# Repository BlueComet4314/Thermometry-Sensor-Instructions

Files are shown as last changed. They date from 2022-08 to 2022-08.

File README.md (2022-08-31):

# Table of Contents

<u>**Intro**</u>
- [Overview of Thermometry Sensors](#overview)
- [Accessories used](#accessories-used)
- [Sensor Board Versions](#sensor-versions)
- [Test data](#tests)
    
    - [Room Temperature Test](#u-room-temp-test-u)
    - [Liquid Nitrogen Test](#u-liquid-nitrogen-test-u)
    - [Vacuum Test](#u-cold-test---inside-vacuum-for-nexo-distillation-column-u)
     
      - [Thermosiphon Set up](#thermosiphon-set-up)

<u>**Instructions**</u>

- [Thermometry Sensor](#thermometry-sensor-1)
- [Thermocouples](#thermocouples)
- [PT100 (RTD) Boards](#pt100-rtd-boards)

  - [RTD Sensor](#sensor)
  - [Parts](#parts)
  - [Oshpark Schematic](#oshpark-schematic)
- [Wiring](#wiring)

  - [QWIIC cables to 3 Wire cable](#pt100-board-to-db15-wires-3-wire-configuration)
  - [DB15 Connector Layout for soldering](#db15-layout)

    - [Visual of wires connected to DB15](#to-db-15-images)
- [Casing](#casing)

- [Test Board](#test-board)

<u>**Final Documentation**</u>

- [Set-up Instructions](#set-up-instructions)
- [Final Images](#final-images)
- [Flange](#flange)
- [Trouble Shooting](#trouble-shooting)

# Overview

## [Original Github - bungernut/nEXO_Thermometry](https://github.com/bungernut/nEXO_Thermometry)

These sensor boards were built to read and display thermometry data. They were orignialy used for an experiment made by LUX-ZEPPLIN (LZ) to measure data within their cryogenic systems. Later, a group from the nEXO group based their design (with permission) off of the group from LZ. 

This document details the process of parts, construction, set-up, and uses of these boards for the nEXO experiment at the SLAC National Accelerator Laboratory. The boards at nEXO are used for cryogenic purposes inside of a cryogenic distillation column. 

**Please don't hesitate to contact me with any questions you may have!!**

The Thermometry Boards are able to detect temperature, pressure, and humidity using five Adafruit MAX31865, two MAX31856 boards (Thermocouple Amplifires), and one BME 280.

The pads are soldered to a small .5" circuit board and connected to the main Thermo board through a series of cables (which will be detailed out below). The small PT100 boards contain a 4-40 sized hole for a small screw, which will allow the boards to be attached to specific places inside of the cryogenic system (more into this later). 
The thermocouples are attached to two Adafruit MAX31856 - Thermocouple Amplifier boards. 

[Back to Top](#table-of-contents)

# Accessories used

## Thermometry Sensor:

### - Normal parts
| LOC | Part | Digikey PN |
| -- | -- | -- |
| J1 |  DB15 | LD15S33E4GV00LF-ND |
| J2 | Barrel 2x5.5mm | CP-002A-ND |
|Teensy Conn| 24POS RCPT| SAM1093-24-ND|
|Teensy Conn| 6POS 2mm RCPT| 23-0791077002-ND |
|Teensy header| 30POS 2.54mm | S1012EC-30-ND |
|Teensy header| 6POS 2mm | WM20513-ND |
| Ethernet Conn | 100 Base T | 1278-1052-ND |
| LCD Conn | 2x CONN HEADER 14POS | AE11367-ND|
| R1-12 | 22 Ohm 0805 | A126437CT-ND |
| R13 | 0 Ohm 0805 | A106066CT-ND |
| CP1 | 47 uF 1206 | 490-16309-1-ND |
| F1 | 1A Fuse | F6777CT-ND |
| C1 | 0.1 uF Ethernet Cap | BC1084CT-ND |
| MCU1 | 2x 24POS Recpt | SAM1093-24-ND |

### - Sensor Boards
| Board Type | Purpose | Digikey Pin |
| -- | -- | -- |
| Adafruit MAX31865 | RTD | 1528-1804-ND |
| Adafruit MAX31856 | Thermocouple Amplifier | 1528-1772-ND |
| Adafruit BME 280 | Temperature, Humidity, Pressure | 1528-1359-ND |

### - Microcontroller

Teensy 4.1 -
  - 1568-DEV-16771-ND

## - PT100 Boards

### - Equipment

- Need a USBC cable for power and uploading arduino software onto microcontroller
- An Ethernet Cable
- Computer or laptop compatible with Arduino software
- Soldering Iron
- tweezers
- needle nose pliers

[Back to Top](#table-of-contents)

# Sensor Versions

## <u> V1 with old test board: </u>

 


## <u> V2 with new test board: </u>

 

## <u> V3 with test thermocouples and Copper block inputs </u>



(picture of copper blocks)

## <u> V4 - Finished (Final) Board: </u>

- Completed PT100 pads/circuit boards and two thermocouples

 

[Back to Top](#table-of-contents)
# Tests

## <u> Room Temp Test </u>

- With PT100 inputs and short Thermocouples

### readings:

| Sensor | 1st Reading | 2nd Reading | 3rd Reading | Actual temperature | 
| -- | -- | -- | -- | -- |
| RTD 1 | 296.58 K | 296.48 K | 296.31 K |  | 
| RTD 2 | 295.57 K | 295.54 K | 295.64 K |  |
| RTD 3 | 296.08 K | 296.11 K | 296.42 K |  |
| RTD 4 | 296.01 K | 295.98 K | 295.87 K |  |
| RTD 5 | 295.98 K | 295.94 K | 296.04 K |  |
| TC 1 | 295.45 K | 295.53 K | 295.86 K |  |
| TC 2 | 295.09 K | 295.11 K | 295.17 K |  |

## <u> Liquid Nitrogen Test </u>

- With Original Copper PT100 blocks and long Thermocouples
- Finished Thermo Sensor, tested temperature readout with Liquid Nitrogen - ~ 77 Kelvin. 
  - Small margin of error on TCs +/- 3 Kelvin.

Liquid Nitrogen ranfes from 63 K - 77.2 Kelvin

###  Readings:

| Sensor | 1st Reading | 2nd Reading | 3rd Reading | Actual temperature | 
| -- | -- | -- | -- | -- |
| RTD 1 | 76.00 K | 75.97 K | 76.06 K | 77.2 K |
| RTD 2 | 76.18 K | 76.15 K | 76.27 K | 77.2 K |
| RTD 3 | 76.09 K | 76.09 K | 76.18 K | 77.2 K |
| RTD 4 | 76.03 K | 76.03 K | 76.09 K | 77.2 K |
| RTD 5 | 75.75 K | 75.69 K | 75.72 K | 77.2 K |
| TC 1 | 81.86 K | 81.72 K | 82.15 K | 77.2 K |
| TC 2 | 80.08 K | 80.31 K | 80.28 K | 77.2 K |

## <u> Cold Test - Inside vacuum for nEXO Distillation Column </u>

### Thermosiphon set up:



The thermosiphon acts as an evaporator for the Liquid Xenon Cell in which it is located. The thermosiphon will be pumping Liquid Nitrogen through it's main two tubes connected at the top:



Once the entire distillaiton column is completed, Gaseous Xenon will be pumped into the main chamber (where the Thermosiphon is located) inside of a smaller enclosed space. This is attached directly below the thermosiphon.

PT100 sensors are screwed into specific places on the thermosiphon. To test, we used PT100 sensor blocks used by a different experiment - LZ. We compared the new PT100s (RTDs) to the previous ones - with the knowledge that LZ's worked - in order to discern any unusual readings from the new PT100s.

### ***Note***

When installing RTDs (or anything) inside of the distillation column, it is a good idea to clean with ethanol on kimwipes.

There are two PT100's from LZ, and four PT100s from nEXO. From now on, I will label the new PT100s as RTD, and the old RTDs as LZ. They are labeled on the Thermosiphon as shown:

### Front Side view:



### Back Side view:



LZ1 and RTD 4 are in parallel with each other on the Aluminium block - They should be reading relatively the same temperatures.
LZ2 and RTD 1 are also in parallel with each other on the Copper block - They should be reading the same temperatures as well.

#### **Note:**



- The *top* of the Thermosiphon - (Copper block) is where the cool Liquid Nitrogen will enter, this is the coldest area
    -  RTDs 1 and 2, and LZ 2 are located here
- The *very bottom* of the block (aluminium block) is where the heater is located - the warmest area.
    - RTDs 3 and 4, and LZ 1 are located here

### Set Thermosiphon temperature at 170 K	(Aluminium block).

| PT100 |	Measurement (K) |
| -- | -- |
| RTD1	| 158.16 |
| RTD2	| 147.29 |
| RTD3	| 169.99 |
| RTD4	| 170.31 |
| -- | -- |
| LZ1 |	170.83 |
| LZ2 |	157.61 |

- This is very promising information - RTDs 3 and 4, and LZ 1 are located directly on the heater, reading near exactly 170 K. In addition, LZ1 and RTD4 sensor readings are very close to each other - roughly .5 K apart from one another

[Back to Top](#table-of-contents)

# Instructions: 

# Thermometry Sensor

### OshPark link:

[Thermometry_Board_V2](https://oshpark.com/shared_projects/bG9Ms06A)

### Finished schematic:

 

### Initial Board:



 

Parts:
| LOC | Part | Digikey PN | Color on Schematic |
| -- | -- | -- | -- |
| J1 |  DB15 | LD15S33E4GV00LF-ND | yellow |
| J2 | Barrel 2x5.5mm | CP-002A-ND | Dark Blue |
|Teensy Conn| 24POS RCPT| SAM1093-24-ND| Orange |
|Teensy Conn| 6POS 2mm RCPT| 23-0791077002-ND | Purple |
|Teensy header| 30POS 2.54mm | S1012EC-30-ND | Orange |
|Teensy header| 6POS 2mm | WM20513-ND | Purple |
| Ethernet Conn | 100 Base T | 1278-1052-ND | Red |
| LCD Conn | 2x CONN HEADER 14POS | AE11367-ND| Green |
| R1-12 | 22 Ohm 0805 | A126437CT-ND | -- |
| R13 | 0 Ohm 0805 | A106066CT-ND | -- |
| CP1 | 47 uF 1206 | 490-16309-1-ND | Teal |
| F1 | 1A Fuse | F6777CT-ND | Pink |
| C1 | 0.1 uF Ethernet Cap | BC1084CT-ND | Light Blue circle |
| MCU1 | 2x 24POS Recpt | SAM1093-24-ND | -- |

[Back to Top](#table-of-contents)
## Highlighted Schematic:



 

## Soldering:
The order in that I added pieces (this is not the best order to go in).
- **22 Ohm Resistors** onto pads R1-R12, skipping R-13
- **0 Ohm Resistor** onto R-13 pad
- **DB15 Connector** on the J1 pad
- **LCD Connectors** on the ILI9341TFT1 and ILI9341TFT2 pads
  - Make sure the keying slot is facing the right direction. On the main board, the slot should be facing *toward* the MAX31865 pads and *away* from the Teensy pad.
  - On the **small** board, make sure the slot is facing *away* from the ILI9341TFT3 Through Holes.
- The **1A Fuse** on the F1 pad 
- A **47 uF capacitor** on CP1 pad, below the Fuse.
- **0.1 uF Ethernet Capacitor** on pad C1.
  - The name of the pad isn’t visible on the schematic; the capacitor is next to the Ethernet Plugin
- An **Ethernet plugin** on the Teensy-Ethernet1 pad.
  - The opening of the connector should also be facing *away* from the board.
- A **Black Barrel Power Jack connector** on the J2 pad.
  - Make sure that this connector is also facing the correct direction; the main connector should be facing *away* from the middle of the board
- The **Receptacle Connectors** are placed on the long row of ThroughHole pins on the Teensy pad:

 

- Similarly, long **connector headers** (length 24) and smaller (3x2) connector headers will be soldered to the Teensy 4.1 board:
  - The 3x2 connector has it's *shortest* side soldered to the Teensy
  - The long 24 pin connector has it's *longest* side solder to the Teensy

 

- The pins (connected to the Teensy) will be put into the Recepticle connectors already soldered to the main board:

  

[Back to Top](#table-of-contents)

### Sensor Boards:

#### Parts Used

| Board Type | Purpose | Digikey Pin | Amount |
| -- | -- | -- | -- |
| Adafruit MAX31865 | Resistance Temperature Detector | 1528-1804-ND | Five |
| Adafruit MAX31856 | Thermocouple Amplifier | 1528-1772-ND | Two |
| Adafruit BME 280 | Temperature, Humidity, Pressure Detector | 1528-1359-ND | One |

- Five Adafruit MAX 31865 boards (Resistance Temperature Detectors (RTDs)) are soldered to their respective places along one end of the main board.
  - These for pin holes are normally where two wire clamps would go. However, instead, we are going to put 3 Connector headers here.  The MAX 31865 boards do not have Connectors that are wide enough for the 4 pins, so break apart the receptacle headers into singular pieces.



  

The individual pins will go in three specific places; one pin in the F- hole, one in the RTD+, and the last in th F+ hole. The front of the Adafruit board has just the F- and F+ label - the RTD+ hole is directly to the left of the F+ slot (see image). The full labels can also be seen on the very back. 







- Two Adafruit MAX31856 boards (Thermocouple Amplifiers) are soldered to other side of board:

 

- One BME 280 Board (Temperature, Humidity, Pressure):




## MAX31856 - RTD Board
- The RTD boards (in our version) were modified for a 3 wire configuration.
- Initially, the connection line on the copper plates - between the 4 and 3 wire pads (ass seen in below images) - needs to be severed.
  - Taking an exact-o knife, the copper line is cut/scraped away.

## Before

 

 

## After


 
 

- The two 3 wire pads need to then be soldered together



Nothing needs to be changed for the BME or Thermocouple amplifiers

[Back to Top](#table-of-contents)

# Thermocouples

The thermocouples used in this sensor are type 'T', with Copper and Constantan (Cu-Con) metals. This type of thermocouple can measure tempuratures from -250 degrees Celsius (23.15 K) to 350 degrees Celsius (623.15 K), which is very helpful to measure accurate temperatures in cryogenic conditions.

Thermocouples themselves always consist of two different types of metals that are joined together at one end - whether with solder or welding is up to the person. When the soldered end of the thermocouple is heated or cooled a voltage is created that can be associated with a specific temperature.

The thermocouples in our system will be used in conjunction with the Adafruit MAX31856 (Thermocouple Amplifier) boards. We'll need two - preferably long (roughly two and a half feet long) in order to test temperature readings. You can also make two short thermocouples in order to quickly test room temperature without the hastle of the long wires.

First, strip both ends of the thermocouple wires - the outer plastic, then the individuals (as shown in the images below).

Leave one side of the wire alone, that will be inserted into the connectors on the thermocouple amplifiers.
On the other end, twist the two metals and solder the wires together.

 
 

  

The two ends that were not soldered together will be inserted into the terminal block (the black fastener), the Copper wire will be placed in the positive port (right hole) and the Constantan wire will be placed into the negative port (left hole).

Screw the top until the wires rest tightly inside the terminal block.

 



Full Sensor with short thermocouples and Test board:



Full sensor with long thermocouples, connected to copper sensor blocks:



[Back to Top](#table-of-contents)

# PT100 (RTD) Boards

These boards were designed to measure and read out temperatures taken from a PT100 (RTD) sensor, which is transmitted to the Adafruit MAX 31865 boards using a QWIIC JST Conncector. The board itself is designed to lever and flatten the white RTD pad against the surface of an object (as seen in images below). 

The board was designed with a 4-40 screw hole in order to lever the PT100 pads onto the surface (in nEXO's case - the Thermosiphon as explained [above](#thermosiphon-set-up)):





----




Full Set Up







### Boards:



### Sensor:



---
## Parts:
---

| Part | Store | Pin |
| -- | -- | -- |
| PT100 - RTD | Digikey | 1759-1021-ND |
| Qwiic JST Connector | Mouser Electronics | 474-PRT-16766 |
| 4 Position Cable | Digikey | 1568-PRT-17257-ND |

[Back to Top](#table-of-contents)

### <u> OshPark Schematic:</u>

[PT100 Level Board - V2](https://oshpark.com/shared_projects/1DKsv6yt)

### <u> Instructions:</u>

Only two parts need to be soldered to the PT100 board; the QWIIC connector and the Resistance Temperature Detector (RTD). 

There are two small holes where the wires of the RTD will be placed through.
When placing the wires in, make sure that the white side of the RTD is facing toward the 4-40 hole and the blue side is facing away from it. That way when the pad is bent, the white side will be facing upward.



Next is the surface mounted QWIIC connector.
The pins should be soldered in their respective places, including the pins on the back of the connector:



### ***Note 1***

Mke sure that the RTD is pulled through the two holes on the PT100 board as far as possible without breaking it.
When bent, the two wires may still jut out a bit on the copper side of the board, we don't want any metal touching the wires and causing a short (see image):

### ***Note 2***

Make sure that the ends of the RTD wires are clipped after you solder. Leaving the wires hanging can also cause a short if they touch any metal.

### <u> Comparisons: </u>

with penny:




 

[Back to Top](#table-of-contents)

### <u>completed</u>

 

back 

side 

Make sure that the ends of the RTD wires after soldered are snipped short.

[Back to Top](#table-of-contents)

full comparisons:

     



[Back to Top](#table-of-contents)

# Wiring

## PT100 Board to DB15 wires (3 wire configuration)

### Materials:

- Heat-shrink
- Three Wire cable
- 4 position cable (digikey)

The PT100 wires are connected to the Adafruit board with a 3 wire configuration. 
The four position (4P) cable bought from digikey site contains four wires and has two male QWIIC connectors on either side - the length of the wire will need to be cut in half.

---

The reason for a 3 wire configuration over simply just having two has to do with the added resistance in the wires themselves. 



In a three or four wire configuration, the extra third and fourth wires detect the added resistance in the main (1st and 2nd) wires so that we are able to later account for it. 
However, a four wire configuration is very complicated to put together. 
Therefore, a 3 wire config is used. 

With a 3 wire, we assume that the added resistance in the first wire is the same as what is detected in the third wire.

More information on these configurations can be found [<u><big>***here***</u></big>](https://www.omega.com/en-us/resources/rtd-2-3-4-wire-connections)

---

As seen in the below photos, the blue wire from the 4P cable was folded back, the three left were stripped and tinned.

Three wire braided cable can be used to make the 4P cable longer. For the nEXO group, 25 inch wire was needed, but the 4P wires were only 6 inches. Measure and cut needed length as necessary.

### _**Note**_:

The colors of the three wire cable doesn't matter, but it would be better to find colors that match with the QWIIC (4P) cable (or any other cable used) to keep colors consistent and easy to follow for later on.

Recommended colors would be - black, red, and white cable. 
The 4P cable is colored black, red, blue, and yellow, but the blue wire was not used; red to red, black to black, and yellow to white.

 The 3 wire cable was also stripped and tinned, but before soldering them together, make sure heat shrink plastic tubes are put on the individual wires. 
 The heat shrink should be think enough to fit over the wire and still have some room to maneuver. 
 It should then be soldered to the 4P cable as seen in the images below.

 The other end of the three wire should not be soldered to anything yet.





[Back to Top](#table-of-contents)

Move the heat shrink so that it covers the exposed wire and both cables that were soldered together. 
Heat the shrink plastics so that they are snug on the wires and do not individually move.
The wires can all three be moved in front of the heat gun at the same time, as long the heat shrink plastics are not touching each other.

Then, cut another piece of heat shrink and place it over the three wire cable (white, red, black) all the way until just before the the soldered joints - not entirely over the connected wires. 
This is to help keep the wires themselves protected and to keep them held together.
It is circled in the next photo:



This also needs to be shrunk with the heat gun. Another wider tube of heat shrink needs to be cut. this time placed over the entirety of the wires - **_including_** the blue wire that was not used from the 4P QWIIC cable. The blue wire is included so that there are no exposed wires - to protect it and the system from shorts.

More heat shrink tubes can be added anywhere on the long strips of wires to keep the three cables together. I recommend putting a piece somwhere in the middle of the 3 wire and, on the opposite side, a little over an inch from the end.



Circled in blue are both the soldered ends of the 3 wire and 4P QWIIC connectors and the placement of the heat shrink. This is one of the final set ups for the Thermometry Sensor. The male connector will be placed in the female QUIIC connector on the PT100 boards.

### Finished:



[Back to Top](#table-of-contents)

# DB15 Layout

## [DB15 Wiring to RTD(Adafruit) boards](https://github.com/BlueComet4314/Test-Board-Instructions)

### To DB-15 (Images)








[Back to Top](#table-of-contents)

# Casing

[Back to Top](#table-of-contents)

# Test Board

Test boards for the Thermometry sensors boards were built in order to assay the functionality of the Thermometry boards as they were constructed.
These test boards (as shown in figure \ref{v2testboard}) use five resistors, with a resistance of 100 ohms (\Omega). The thermometry sensors - through the Teensy-4.1 - are able to convert this resistance to temperature.

Test Board wiring is the exact same as the wiring for the PT100/QWIIC cables found [here](#db15-layout)

## --> [DB15 Wiring to RTD(Adafruit) boards](https://github.com/BlueComet4314/Test-Board-Instructions) <--

### ***Version 1***

   

### ***Version 2***

  

## ***Connected to Thermometry Sensor***



[Back to Top](#table-of-contents)

# Teensy Code

***Full Teensy Code and info can be found [***here***](https://github.com/BlueComet4314/Thermometry-Sensor-Instructions/tree/main/Teensy_code%20for%20Microcontroller) or in files at the top of the repository***

[Back to Top](#table-of-contents)

# Set-up Instructions

## With Test Board

Plug in the initial components before supplying the main board with power (just in case there are any shorts)

1. Ethernet Cable into ethernet port
2. Test Board into DB15 connector on Thermosensor
3. Main screen needs to be connected to middle port.
4. Thermocouples need to be screwed into the terminal block (the black fastener on the main board)
  
    -  ***Remember!!*** The Copper wire will be placed in the positive port (right hole) and the Constantan wire will be placed into the negative port (left hole).



After plugging in the components, supply power to the board, whether this is a usb cable inserted into the Teensy or a power adaptor into the barrel connector, it doesn't matter.
***However***, make sure that if you use a power adaptor that it does **not** excede <u>**6 Volts**</u>. This can cause damage to the Teensy or other parts of the Thermosensor.

[Back to Top](#table-of-contents)

## With PT100s attached to a surface

PT100 cables were connected to inner vacuum flange.
Gender changer for the DB15 was welded onto flange which connects RTDs from inside the vacuum chamber to a cable outside in open air.
Outer cable connects to main thermometry board.

The PT100 boards themselves are going to be inside the distillation column at SLAC taking in temperature readings. 

<big>***Make sure that these PT100s are being cleaned before being placed inside the column***</big>

The boards will be attached to specific places inside of the cryogenic system. As said above, the hole on the PT100 is a type 4-40 for a small screw which levers/flattens the RTD sensor against the surface at any point in the column.

When attaching the sensors, make sure that the boards arent overly tightened. 
They should be tight enough that the board is snug and does not move when pushed or twisted.
The RTD sensor should not be so tight against the surface that it gets squished. 
Tighten the screw until finger tight, then screw one or two more turns.
Should only be tightened enough that the board is secure and doesn't budge.




---





[Back to Top](#table-of-contents)

# Final images

## Test 1 -  Initial Room Temperature Testing of fully connected board

PT100s and Thermocouples were left in open air, taking in temperature of the room.






## Test 2 - Sensors inside Liquid Xenon Cell, attached to Thermosiphon

PT100s were attached to the Thermosiphon, as shown [here](#thermosiphon-set-up). The liquid xenon cell was placed under vacuum, Nitrogen gas was set to flow through the thermosiphon's lines, and temperature on the thermosiphon set to 170 degrees Kelvin (-103.15 Celsius/-153.67 Fahrenheit).



Initial cooldown, first readings of room temperature. 



Thermosiphon has cooled to 170 K.

RTDs 1-4 are located at different positions on the thermosiphon as shown in image [one](#back-side-view) and [two](#front-side-view). 
RTDs 1 and 2 are near the top where it's the coldest, 3 and 4 are near the bottom where the heater on the Thermosiphon is located. 
RTD 1 is in between 2 and 3.

They will have slightly differing temperatures from each other, with the exception of 3 and 4.
 3 and 4 are located on the Aluminium block directly opposite from each other - they should have very similar readouts.






Graphing as the PT100 sensors (only 4 were used in this test) were cooled to 170 degrees Kelvin.

## Test 3 - Overnight test inside LXe Cell



Initial check in the evening before being left overnight to fully cool.



Graph of the complete cooldown of the RTD temperatures - stopping to rest at roughly 83 K to 85 K

Nitrogen gas was set to flow through the thermosiphon lines to cool the thermosiphon itself. The temperature of N2 is roughly 77 degrees Kelvin (-350 Fahrenheit/-196 Celsius). 

The graph in the second image shows the successful cooldown to Nitrogen Temperature. As shown in the top image, the RTDs (from nEXO) and LZs (from LUX-ZEPPLIN) show matching temperatures. Since we knew that LZ's PT100 sensors did work, to see nEXO's RTDs reading out near identical readings was promising!

## Updates -  "Room temperature" Check



Quick check on thermometry sensors a few days after system's temperature was brought out of 77 K and let to rise back to room temperature.

Both Temperature Sensors that are being used now have their own protective cases.

## Updates - Second Room temperature check

After five days, the RTD sensors were once again check to make sure readings were accurate to the LZ sensors and that things were still running smoothly.



[Back to Top](#table-of-contents)

# Flange

**This section is only if the Thermometry Sensors are being used for a cryogenic system with metal connector flanges. The metal flanges are essentially used in order to connect a DB15 cable to the PT100 wires while keeping the PT100s inside vacuum and the cable in open air as seen in the photos below.**

**If not used for a cryogenic system, this section can be skipped.**

PT100 cables were connected to an inner vacuum flange (feedthrough).



Gender changer for the DB15 was welded onto the flange which connects the RTDs from inside of the chamber to a cable outside of the chamber. The outer cable then connects to main thermometry board. 

In the nEXO system, there was a small issue with the feedthrough connector. 
The pins at the center were not direct feed throughs.
In other words, out of 15 pins; pin 15 on the vacuum side of the flange did not directly connect to pin 15 on the open air side.
The pin connections were flipped; pin 15 connected to pin 9, pin 1 connected to pin 8, etc.

You can also test this using a multimeter, setting it to 'Continuity' mode - the mode that makes a sound when there is a charge or current running through. Place one probe on the vacuum pins and the second on the open air pins - testing each vacuum pin with its corresponding open air pin (15 to 15, 8 to 8, 3 to 3, etc.). 

Therefore, if you have soldered the DB15 connector correctly according to the schematic and you are unable to read temperature readouts when the feedthrough flange is connected, this may be your issue.

Fortunately, this is an easy fix. 
_Un_ fortunately, you will have to solder the DB15 wires backwards. 

The easiest way to do this, is to take another DB15 connector/cable and face the connecting side upwards and have it nearby:





The second DB15 connector/cable will be there as a guide to look at as you solder the wires. 
Instead of following the numbers on the connector you are soldering on, follow the numbers on the other DB15 connector.
It will be the same soldering method, except backwards.

After this however, you will no longer be able to test the Thermometry boards without the feedthrough flange as the genderswapper.
The normal gender swapper doesn't have flipped pins (15 _is_ connected to 15, 5 to 5, etc.).

I suggest having an extra set of QWIIC cables connected to a DB15 that is soldered the normal way. 
That way if you need to test/assay something on the main thermo sensor board or PT100 board, you won't need the metal flange and extra cable to do so.

[Back to Top](#table-of-contents)

# Trouble Shooting

## Teensy

1. If you plug in the power source at some point and the green light on the Teensy blink on once briefly before dimming immediately to a faint green, this means that the Teensy may have been damaged/shorted.
You can easily check this if you have another Teensy on hand, the Teensys are designed to be able to be removed from the pins it is connected to just in case. 
You can pull the old Teensy off and replace it with a new one (once again uploading the Thermometry/Teensy code) and test it.

    - Another way to see if this is a Teensy issue, is if the screen itself doesn't display anything.
  It would only briefly light up once the power is supplied, then immediatly go black. 

2. If you have made multiple different thermometry sensors - or even if you have only made one - make sure that you have changed the MAC and I.P. address according to your own system/server, and that they are different from one another.

## Attaching PT100s to a surface

1. If you are attaching the PT100s to a surface and you can't find a short enough screw, sometimes it is easier to use a washer to shorten the length of a long screw.
**However, make sure that the washer does not touch any metal or solder on the board.** 
This could short the small boards and you won't see any temperature readouts. 

## Temperature readouts

If you  aren't seeing any temperature readouts:
1. a short may be an issue. 
Make sure that there is no metal touching any of the RTD sensors or solder on the small boards. 
The shorts won't destroy any boards, but it'll cause irregularities in your readings.

2. You may have a problem with the flange as explain in **[the section on the vacuum gender swapper flange here](#flange)**

## 

[Back to Top](#table-of-contents)

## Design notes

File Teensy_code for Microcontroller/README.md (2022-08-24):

# Teensy Code - what it's for

The code in the teensy_tft file needs to be uploaded to the Teensy 4.1 microcontroller used on the Thermometry Sensor board

This code essentially takes in the resistance/temperature readings from the PT100 (RTD sensors), converts the resistance to temperature in Kelvin, then displays this information to the digital screen that is connected to the main board.
The code is written in C++.




Programs used for uploading teensy code to the microcontroller can be found [here](https://www.pjrc.com/teensy/loader_mac.html).

This link will take you to the following page:



Download the two Teensy Loader links (boxed in red) and install the packages - One is the Teensyduino application and a second loader just called Teensy:



"Teensy" is the left application, "Teensyduino" is the right.

The website will instruct you on how to download these apps.

### ***Note  #1*** 

The Teensy app (left side of above image) does not directly get downloaded into your applications folder.
I'd recommend dragging and placing it there so you don't have to go searching for it.

The teensy_tft file in this repository will be opened through the Teensyduino application. 
When uploading the teensy_tft file, make sure that you are uploading a ***.zip*** file and not a folder.
When the files here are downloaded from this repository, they will already be in a .zip format.
Upload the teensy code exactly how it is downloaded.

### ***Note #2***

You will also need to change the I.P. and MAC address in the code itself according to your own system/server. Currently, there are three separate I.P.s and MAC addresses commented out in lines $35 - 49$. In the nEXO system, we built three thermometry sensors, each needed its own I.P. and MAC address.

The IP address will be dependent on your local network.



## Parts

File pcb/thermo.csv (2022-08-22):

Reference | Quantity | Value | Footprint | Datasheet
0.1uF1 | 1 | C1 | Capacitor_THT:C_Disc_D3.0mm_W1.6mm_P2.50mm | Digikey BC1084CT-ND
ADC1 ADC2 ADC3 ADC4 ADC5 | 5 | PT100 | Thermometry:MAX31865
ADC6 | 1 | thermocouple1 | Thermometry:MAX31856
ADC7 | 1 | thermocouple2 | Thermometry:MAX31856
CP1 | 1 | 47uF | Capacitor_THT:CP_Radial_D5.0mm_P2.00mm | 2368-VHT47M25-ND
F1 | 1 | 1A | Thermometry:thermo_fuse | https://www.digikey.com/en/products/detail/littelfuse-inc/0154001-DRTL/2520456
ILI9341TFT1 ILI9341TFT2 | 2 | Conn_01x14 | Thermometry:ILI9341_2x7_connector | ~
ILI9341TFT3 | 1 | Conn_01x14 | Thermometry:ILI9341_1x14_connector | ~
J1 | 1 | DB15_Female | Thermometry:D15_Female_Horizontal | ~
J2 | 1 | Barrel_Jack | Connector_BarrelJack:BarrelJack_Horizontal | https://www.digikey.com/en/products/detail/cui-devices/PJ-002A/96962
MCU1 | 1 | Teensy4.1 | Thermometry:Teensy41
R1 R2 R3 R4 R5 R6 R7 R8 R9 R10 R11 R12 | 12 | 22 | Resistor_SMD:R_0805_2012Metric_Pad1.20x1.40mm_HandSolder | ~
R13 | 1 | 0 | Resistor_SMD:R_0805_2012Metric_Pad1.20x1.40mm_HandSolder | ~
Teensy_Ethernet1 | 1 | RJ45_LED | Connector_RJ:RJ45_Cetus_J1B1211CCD_Horizontal | ~
U1 | 1 | BME280 | Thermometry:BME280

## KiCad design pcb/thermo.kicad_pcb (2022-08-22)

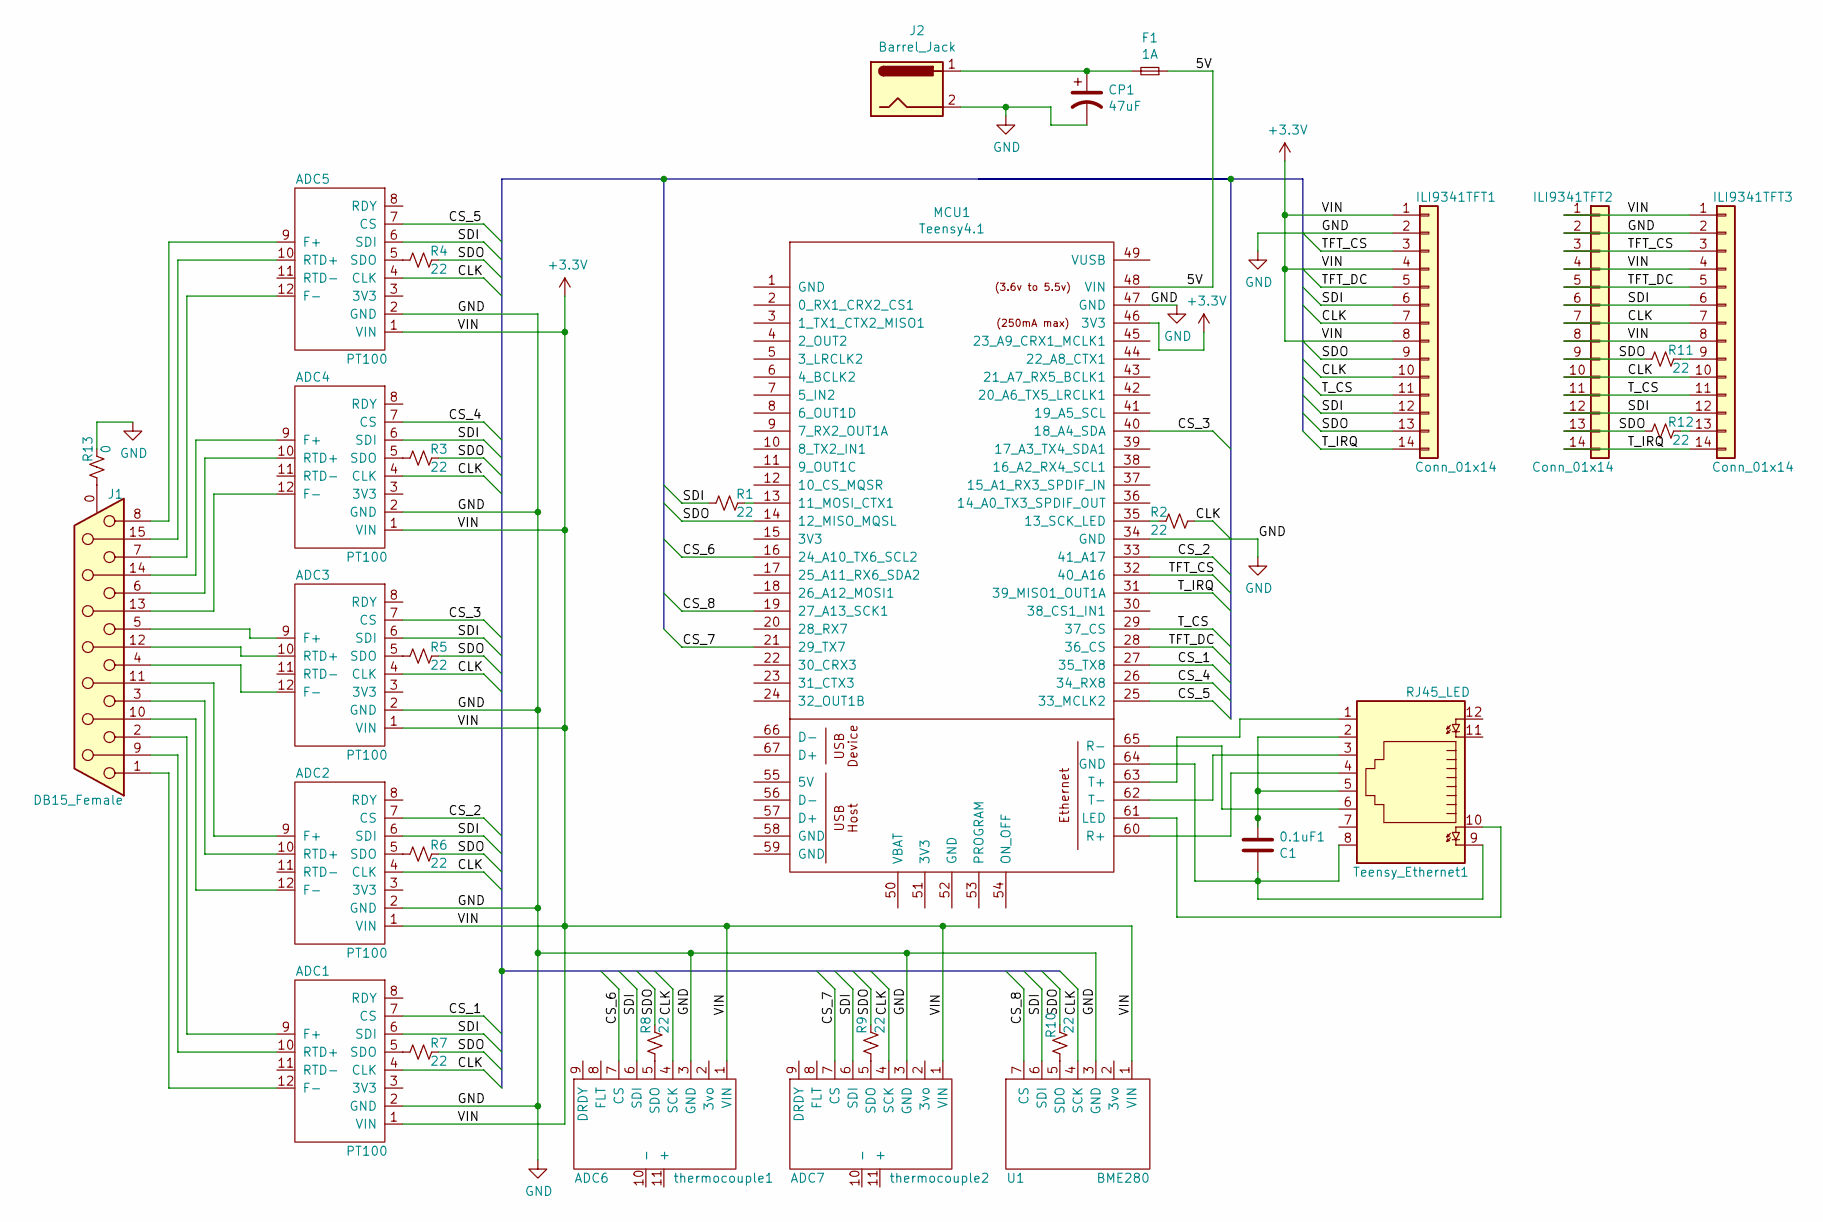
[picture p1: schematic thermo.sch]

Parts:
0.1uF1: C1; C_Disc_D3.0mm_W1.6mm_P2.50mm
ADC1, ADC2, ADC3, ADC4, ADC5: PT100; MAX31865
ADC6: thermocouple1; MAX31856
ADC7: thermocouple2; MAX31856
CP1: 47uF; CP_Radial_D5.0mm_P2.00mm
F1: 1A; thermo_fuse
ILI9341TFT1, ILI9341TFT2: Conn_01x14; ILI9341_2x7_connector
ILI9341TFT3: Conn_01x14; ILI9341_1x14_connector
J1: DB15_Female; D15_Female_Horizontal
J2: Barrel_Jack; BarrelJack_Horizontal
MCU1: Teensy4.1; Teensy41
R1, R2, R3, R4, R5, R6, R7, R8, R9, R10, R11, R12: 22; R_0805_2012Metric_Pad1.20x1.40mm_HandSolder
R13: 0; R_0805_2012Metric_Pad1.20x1.40mm_HandSolder
Teensy_Ethernet1: RJ45_LED; RJ45_Cetus_J1B1211CCD_Horizontal
U1: BME280

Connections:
+3V3: ADC1.1 (VIN), ADC2.1 (VIN), ADC3.1 (VIN), ADC4.1 (VIN), ADC5.1 (VIN), ADC6.1 (VIN), ADC7.1 (VIN), ILI9341TFT1.1, ILI9341TFT1.4, ILI9341TFT1.8, ILI9341TFT2.1, ILI9341TFT2.4, ILI9341TFT2.8, ILI9341TFT3.1, ILI9341TFT3.4, ILI9341TFT3.8, MCU1.46 (3V3), U1.1 (VIN)
/5V: F1.1, MCU1.48 (VIN)
/CLK: ADC1.4 (CLK), ADC2.4 (CLK), ADC3.4 (CLK), ADC4.4 (CLK), ADC5.4 (CLK), ADC6.4 (SCK), ADC7.4 (SCK), ILI9341TFT1.7, ILI9341TFT1.10, ILI9341TFT2.7, ILI9341TFT2.10, ILI9341TFT3.7, ILI9341TFT3.10, R2.1, U1.4 (SCK)
/CS_1: ADC1.7 (CS), MCU1.27 (35_TX8)
/CS_2: ADC2.7 (CS), MCU1.33 (41_A17)
/CS_3: ADC3.7 (CS), MCU1.40 (18_A4_SDA)
/CS_4: ADC4.7 (CS), MCU1.26 (34_RX8)
/CS_5: ADC5.7 (CS), MCU1.25 (33_MCLK2)
/CS_6: ADC6.7 (CS), MCU1.16 (24_A10_TX6_SCL2)
/CS_7: ADC7.7 (CS), MCU1.21 (29_TX7)
/CS_8: MCU1.19 (27_A13_SCK1), U1.7 (CS)
/SDI: ADC1.6 (SDI), ADC2.6 (SDI), ADC3.6 (SDI), ADC4.6 (SDI), ADC5.6 (SDI), ADC6.6 (SDI), ADC7.6 (SDI), ILI9341TFT1.6, ILI9341TFT1.12, ILI9341TFT2.6, ILI9341TFT2.12, ILI9341TFT3.6, ILI9341TFT3.12, R1.2, U1.6 (SDI)
/SDO: ILI9341TFT1.9, ILI9341TFT1.13, ILI9341TFT2.9, ILI9341TFT2.13, MCU1.14 (12_MISO_MQSL), R3.1, R4.1, R5.1, R6.1, R7.1, R8.1, R9.1, R10.1, R11.2, R12.2
/TFT_CS: ILI9341TFT1.3, ILI9341TFT2.3, ILI9341TFT3.3, MCU1.32 (40_A16)
/TFT_DC: ILI9341TFT1.5, ILI9341TFT2.5, ILI9341TFT3.5, MCU1.28 (36_CS)
/T_CS: ILI9341TFT1.11, ILI9341TFT2.11, ILI9341TFT3.11, MCU1.29 (37_CS)
/T_IRQ: ILI9341TFT1.14, ILI9341TFT2.14, ILI9341TFT3.14, MCU1.31 (39_MISO1_OUT1A)
GND: ADC1.2 (GND), ADC2.2 (GND), ADC3.2 (GND), ADC4.2 (GND), ADC5.2 (GND), ADC6.3 (GND), ADC7.3 (GND), CP1.2, ILI9341TFT1.2, ILI9341TFT2.2, ILI9341TFT3.2, J2.2, MCU1.34 (GND), MCU1.47 (GND), R13.1, U1.3 (GND)
unnamed: 0.1uF1.1, Teensy_Ethernet1.2, Teensy_Ethernet1.5
unnamed: 0.1uF1.2, MCU1.64 (GND), Teensy_Ethernet1.8, Teensy_Ethernet1.9
unnamed: ADC1.5 (SDO), R7.2
unnamed: ADC1.9 (F+), J1.2
unnamed: ADC1.10 (RTD+), J1.9
unnamed: ADC1.12 (F-), J1.1
unnamed: ADC2.5 (SDO), R6.2
unnamed: ADC2.9 (F+), J1.11 (P111)
unnamed: ADC2.10 (RTD+), J1.3
unnamed: ADC2.12 (F-), J1.10
unnamed: ADC3.5 (SDO), R5.2
unnamed: ADC3.9 (F+), J1.5
unnamed: ADC3.10 (RTD+), J1.12
unnamed: ADC3.12 (F-), J1.4
unnamed: ADC4.5 (SDO), R3.2
unnamed: ADC4.9 (F+), J1.14
unnamed: ADC4.10 (RTD+), J1.6
unnamed: ADC4.12 (F-), J1.13
unnamed: ADC5.5 (SDO), R4.2
unnamed: ADC5.9 (F+), J1.8
unnamed: ADC5.10 (RTD+), J1.15
unnamed: ADC5.12 (F-), J1.7
unnamed: ADC6.5 (SDO), R8.2
unnamed: ADC7.5 (SDO), R9.2
unnamed: CP1.1, F1.2, J2.1
unnamed: ILI9341TFT3.9, R11.1
unnamed: ILI9341TFT3.13, R12.1
unnamed: J1.0 (PAD), R13.2
unnamed: MCU1.13 (11_MOSI_CTX1), R1.1
unnamed: MCU1.35 (13_SCK_LED), R2.2
unnamed: MCU1.60 (R+), Teensy_Ethernet1.4
unnamed: MCU1.61 (LED), Teensy_Ethernet1.10
unnamed: MCU1.62 (T-), Teensy_Ethernet1.3
unnamed: MCU1.63 (T+), Teensy_Ethernet1.1
unnamed: MCU1.65 (R-), Teensy_Ethernet1.6
unnamed: R10.2, U1.5 (SDO)

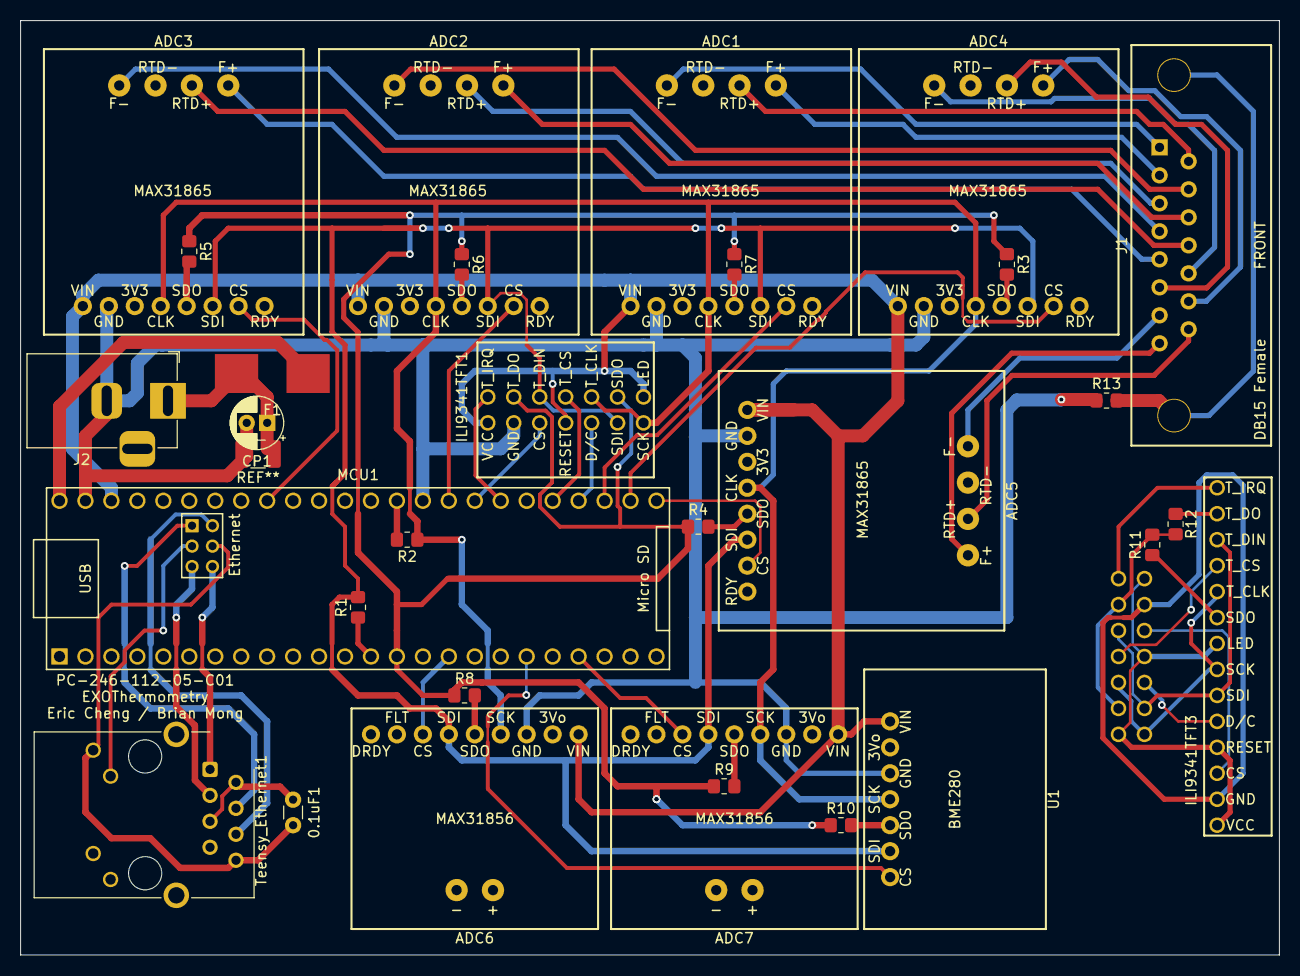
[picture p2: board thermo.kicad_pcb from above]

Board: 2 copper layers, 123.2 x 91.4 mm, 31 parts (1 on the bottom side), 54 nets.

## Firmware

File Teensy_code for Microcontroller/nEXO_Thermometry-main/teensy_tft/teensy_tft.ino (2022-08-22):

#include <Watchdog_t4.h>

#include <Adafruit_MAX31865.h>
#include <Adafruit_MAX31856.h>
#include <Adafruit_BME280.h>
#include <Wire.h>
#include <SPI.h>
#include "ILI9341_t3.h"
#include <NativeEthernet.h>
#include <Arduino.h>
#include <ArduinoRS485.h> // ArduinoModbus depends on the ArduinoRS485 library
#include <ArduinoModbus.h>
#include <Watchdog_t4.h>

WDT_T4<WDT1> wdt;

#define RREF      430.0
#define RNOMINAL  100.0
Adafruit_MAX31865 rtd01 = Adafruit_MAX31865(35);
Adafruit_MAX31865 rtd02 = Adafruit_MAX31865(41);
Adafruit_MAX31865 rtd03 = Adafruit_MAX31865(18);
Adafruit_MAX31865 rtd04 = Adafruit_MAX31865(34);
Adafruit_MAX31865 rtd05 = Adafruit_MAX31865(33);
Adafruit_MAX31856 tcp01 = Adafruit_MAX31856(24);
Adafruit_MAX31856 tcp02 = Adafruit_MAX31856(29);
Adafruit_BME280 bme(27); // hardware SPI

#define VERSION "nEXO Thermometry v1.5"
#define TFT_DC 36
#define TFT_CS 40
#define T_CS 37
#define T_IRQ 39
ILI9341_t3 tft = ILI9341_t3(TFT_CS, TFT_DC);

// Enter a MAC address for your controller below.

// Thermo Sensor 1
// byte mac[] = {0xDE, 0xAD, 0xBE, 0xEF, 0xFE, 0xE1};
//// The IP address will be dependent on your local network:
//IPAddress ip(192,168,1,81);

// Thermo 2
// byte mac[] = {0xDE, 0xAD, 0xBE, 0xEF, 0xFE, 0xE2};
// IPAddress ip(192,168,1,82);


// Thermo 3
//byte mac[] = {0xDE, 0xAD, 0xBE, 0xEF, 0xFE, 0xE3};
//IPAddress ip(192,168,1,83);


EthernetServer ethServer(502);
EthernetClient client;
ModbusTCPServer modbusTCPServer;

uint32_t currentMillis;
uint32_t wdtfeedMillis;
uint32_t pollModbusMillis;
uint32_t updateSensorsMillis;
uint32_t updateClientMillis;
uint32_t updateDisplayMillis;

// Global variables to make current sensor temps available to every function
uint16_t rawRTD01;
uint16_t rawRTD02;
uint16_t rawRTD03;
uint16_t rawRTD04;
uint16_t rawRTD05;
float rtd01temp;
float rtd02temp;
float rtd03temp;
float rtd04temp;
float rtd05temp;
float tcp01temp;
float tcp02temp;
float bmeTemp;
float bmePres;
float bmeHumd;

//Modbus holding register address mapping
const int rtd01_reg = 0;
const int rtd02_reg = 1;
const int rtd03_reg = 2;
const int rtd04_reg = 3;
const int rtd05_reg = 4;
const int tcp01_reg1 = 5;
const int tcp01_reg2 = 6;
const int tcp02_reg1 = 7;
const int tcp02_reg2 = 8;
const int bmeTmp_reg1 = 9;
const int bmeTmp_reg2 = 10;
const int bmePrs_reg1 = 11;
const int bmePrs_reg2 = 12;
const int bmeHum_reg1 = 13;
const int bmeHum_reg2 = 14;

union {
    float asFloat;
    uint16_t asInt[2];
} flreg;

void setup() {
  //Serial.begin(9600);
  WDT_timings_t WDTconfig;
  WDTconfig.timeout = 10; /* in seconds, 0->128 */
  WDTconfig.trigger = 2; /* in seconds, 0->128 */
  //WDTconfig.callback = myCallback;
  wdt.begin(WDTconfig);
  
  tft.begin();
  tft.fillScreen(ILI9341_BLACK);
  tft.setTextColor(ILI9341_WHITE);
  tft.setTextSize(3);
  tft.setRotation(3);
  tft.setCursor(10, 10);
  tft.println(VERSION);
  tft.setTextSize(1);
  tft.println("Waiting for Ethernet Connection");

  rtd01.begin(MAX31865_3WIRE);
  rtd02.begin(MAX31865_3WIRE);
  rtd03.begin(MAX31865_3WIRE);
  rtd04.begin(MAX31865_3WIRE);
  rtd05.begin(MAX31865_3WIRE);
  tcp01.begin();
  tcp01.setThermocoupleType(MAX31856_TCTYPE_T);
  tcp02.begin();
  tcp02.setThermocoupleType(MAX31856_TCTYPE_T);
  bme.begin();
  
  // Get the current values for the sensors before serving crap data
  readSensors();
  updateClient(); 

  Ethernet.begin(mac, ip);
  // Check for Ethernet hardware present
  if (Ethernet.hardwareStatus() == EthernetNoHardware) {
    tft.println("Ethernet shield not found.");
    while (true) {
      delay(1); // do nothing, no point running without Ethernet hardware
    }
  }

  // Start the server
  ethServer.begin();
  modbusTCPServer.begin();
  // configure holding registers at address 0x00
  modbusTCPServer.configureHoldingRegisters(0x00, 50);
}


void loop() {
  currentMillis = millis();
  
  client = ethServer.available();
  // listen for incoming clients
  if (client) {
    
    //Serial.println("client=True");
    modbusTCPServer.accept(client);
    while (client.connected()) {
      currentMillis = millis();
      //Serial.println("Client=While-True");
      modbusTCPServer.poll();
      
      if (currentMillis - pollModbusMillis > 100) {
        // poll for Modbus TCP requests, while client connected
        modbusTCPServer.poll();
        pollModbusMillis = currentMillis;
      }
      if (currentMillis - updateSensorsMillis > 500) {
        //Serial.print("Read Sensors...");
        readSensors();
        updateSensorsMillis = currentMillis;
        //Serial.println("Done");
      }
      if (currentMillis - updateClientMillis > 500) {
        //Serial.print("Update Modbus...");
        updateClient();
        updateClientMillis = currentMillis;
        //Serial.println("Done");
      }
      if (currentMillis - updateDisplayMillis > 2000) {
        //Serial.print("Update Display...");
        updateDisplay();
        updateDisplayMillis = currentMillis;
        //Serial.println("Done");
        wdt.feed();
      }
    }
  }
  else {
    // backup for if client disconnects, display still runs
    if (currentMillis - updateDisplayMillis > 2000) {
      readSensors();
      updateDisplay();
      updateDisplayMillis = currentMillis;
      wdt.feed();
    }
  }
}


void readSensors() {
  rawRTD01 = rtd01.readRTD();
  rawRTD02 = rtd02.readRTD();
  rawRTD03 = rtd03.readRTD();
  rawRTD04 = rtd04.readRTD();
  rawRTD05 = rtd05.readRTD();
  
  rtd01temp = rtd01.temperature(RNOMINAL, RREF);
  rtd02temp = rtd02.temperature(RNOMINAL, RREF);
  rtd03temp = rtd03.temperature(RNOMINAL, RREF);
  rtd04temp = rtd04.temperature(RNOMINAL, RREF);
  rtd05temp = rtd05.temperature(RNOMINAL, RREF);
  tcp01temp = tcp01.readThermocoupleTemperature();
  tcp02temp = tcp02.readThermocoupleTemperature();
  bmeTemp = bme.readTemperature();
  bmePres = float(bme.readPressure())/100000.0;
  bmeHumd = bme.readHumidity();
  

  // Change Celsius to Kelvin
  rtd01temp += 273.15;
  rtd02temp += 273.15;
  rtd03temp += 273.15;
  rtd04temp += 273.15;
  rtd05temp += 273.15;
  tcp01temp += 273.15;
  tcp02temp += 273.15;
  bmeTemp += 273.15;
}


void updateClient() {
  if(!rtd01.readFault()){ 
    modbusTCPServer.holdingRegisterWrite(rtd01_reg, rawRTD01);
  }
  else {
    modbusTCPServer.holdingRegisterWrite(rtd01_reg, 0);
    rtd01.clearFault();  
  }
  
  if(!rtd02.readFault()){ 
    modbusTCPServer.holdingRegisterWrite(rtd02_reg, rawRTD02);
  }
  else {
    modbusTCPServer.holdingRegisterWrite(rtd02_reg, 0);
    rtd02.clearFault();
  }
  
  if(!rtd03.readFault()){ 
    modbusTCPServer.holdingRegisterWrite(rtd03_reg, rawRTD03);
  }
  else {
    modbusTCPServer.holdingRegisterWrite(rtd03_reg, 0);
    rtd03.clearFault();
  }
  
  if(!rtd04.readFault()){ 
    modbusTCPServer.holdingRegisterWrite(rtd04_reg, rawRTD04);
  }
  else {
    modbusTCPServer.holdingRegisterWrite(rtd04_reg, 0);
    rtd04.clearFault();
  }
  
  if(!rtd05.readFault()){ 
    modbusTCPServer.holdingRegisterWrite(rtd05_reg, rawRTD05);
  }
  else {
    modbusTCPServer.holdingRegisterWrite(rtd05_reg, 0);
    rtd05.clearFault();
  }

  flreg.asFloat = tcp01temp;
  modbusTCPServer.holdingRegisterWrite(tcp01_reg1, flreg.asInt[1]);
  modbusTCPServer.holdingRegisterWrite(tcp01_reg2, flreg.asInt[0]);
  flreg.asFloat = tcp02temp;
  modbusTCPServer.holdingRegisterWrite(tcp02_reg1, flreg.asInt[1]);
  modbusTCPServer.holdingRegisterWrite(tcp02_reg2, flreg.asInt[0]);
  flreg.asFloat = bmeTemp;
  modbusTCPServer.holdingRegisterWrite(bmeTmp_reg1, flreg.asInt[1]);
  modbusTCPServer.holdingRegisterWrite(bmeTmp_reg2, flreg.asInt[0]);
  flreg.asFloat = bmePres;
  modbusTCPServer.holdingRegisterWrite(bmePrs_reg1, flreg.asInt[1]);
  modbusTCPServer.holdingRegisterWrite(bmePrs_reg2, flreg.asInt[0]);
  flreg.asFloat = bmeHumd;
  modbusTCPServer.holdingRegisterWrite(bmeHum_reg1, flreg.asInt[1]);
  modbusTCPServer.holdingRegisterWrite(bmeHum_reg2, flreg.asInt[0]);  
}


void updateDisplay() {
  tft.fillScreen(ILI9341_BLACK);
  tft.setTextSize(3);
  tft.setTextColor(ILI9341_WHITE, ILI9341_BLACK);
  tft.setCursor(10, 10);
  if(!rtd01.readFault()){ 
    tft.print("RTD_01:"); tft.print(rtd01temp); tft.println(" K");
  }
  else {
    tft.print("RTD_01:"); tft.print("--"); tft.println(" K");
    rtd01.clearFault();
  }
  
  tft.setCursor(10, 40);
  if(!rtd02.readFault()){ 
    tft.print("RTD_02:"); tft.print(rtd02temp); tft.println(" K");
  }
  else {
    tft.print("RTD_02:"); tft.print("--"); tft.println(" K");
    rtd02.clearFault();
  }  
  
  tft.setCursor(10, 70);
  if(!rtd03.readFault()){ 
    tft.print("RTD_03:"); tft.print(rtd03temp); tft.println(" K");
  }
  else {
    tft.print("RTD_03:"); tft.print("--"); tft.println(" K");
    rtd03.clearFault();
  }
  
  tft.setCursor(10, 100);
  if(!rtd04.readFault()){ 
    tft.print("RTD_04:"); tft.print(rtd04temp); tft.println(" K");
  }
  else {
    tft.print("RTD_04:"); tft.print("--"); tft.println(" K");
    rtd04.clearFault();
  }

  tft.setCursor(10, 130);
  if(!rtd05.readFault()){ 
    tft.print("RTD_05:"); tft.print(rtd05temp); tft.println(" K");
  }
  else {
    tft.print("RTD_05:"); tft.print("--"); tft.println(" K");
    rtd05.clearFault();
  }  

  tft.setTextColor(ILI9341_YELLOW, ILI9341_BLACK);
  tft.setCursor(10, 160);
  tft.print("TCP_01:"); tft.print(tcp01temp); tft.println(" K");
  tft.setCursor(10, 190);
  tft.print("TCP_02:"); tft.print(tcp02temp); tft.println(" K");

  tft.setTextColor(ILI9341_WHITE, ILI9341_BLACK);
  tft.setCursor(10, 220);
  tft.setTextSize(1);
  tft.print("BME:"); tft.print(bmeTemp); tft.print("K "); 
  tft.print(bmePres); tft.print("Bar "); tft.print(bmeHumd); tft.println("%");
}

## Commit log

2022-08-16 finished thermocouples, began PT100 and wiring instructions
2022-08-16 PT100 and wiring instructions
2022-08-20 Updated Wiring
2022-08-22 Updated Wiring/Test Board
2022-08-22 Updated Teensy code
    [MAX31865.sch, thermo.csv, thermo.kicad_pcb, thermo.sch]
